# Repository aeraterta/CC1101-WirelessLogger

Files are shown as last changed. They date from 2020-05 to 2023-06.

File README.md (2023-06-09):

# Wireless Data Logging Platform for Human Temperature and Pulse Rate with Networked Mobile Nodes

<p align="center">
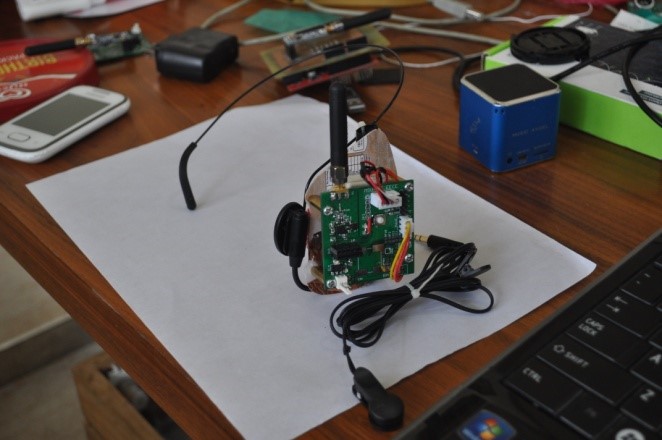
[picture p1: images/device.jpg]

<p>

This is an undergraduate thesis made by Anthony E. Raterta as a requirement for the Degree Bachelor of Science in Electronics and Communications Engineering. 

## Objectives

Generally, the main objective of this study is to construct a prototype of a wireless multi-node data logger that has mobile sensor nodes using transceivers that communicate in the ISM band.

The following are the specific objectives of this study:

1.	To construct a wearable data logger platform.
2.	To utilize the CC1101 transceiver chips for communication.
3.	To attach a temperature and pulse rate sensor in the data logger platform for monitoring human body temperature and pulse rate. 
4.	To identify a suitable location for human body temperature and pulse rate monitoring.

## Methods 

### Flow

The operation of the system imposed is shown in the image below. It contains simplified illustration of the two major parts, the mobile sensor node which may be of any number but for the study, the researcher only made two nodes. The other major part of the system is the receiver node which receives the packets sent by both sensor nodes and dummy nodes.

<p align="center">
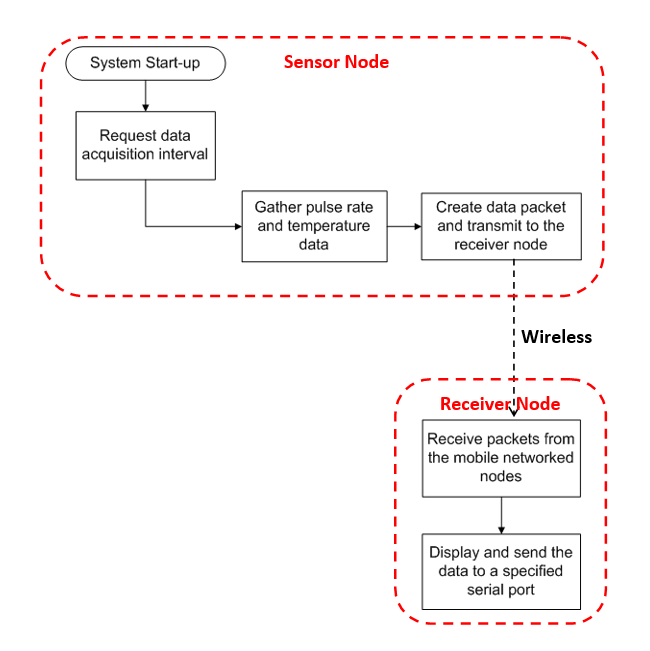
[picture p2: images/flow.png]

<p>

### Block Diagram

Shown in the image below is the physical architecture of the system designed to gather temperature and pulse rate of a patient at an interval set. A single sensor node is composed of an MLX90614 infrared thermometer and an infrared based Grove ear-clip pulse rate sensor.  These modules serve as input devices to an ATmega328p microcontroller unit with a CC1101 RF transceiver working at 433 mega hertz frequency band connected into it and to have the data gathered transmitted into the receiver node which is composed of a CC1101 RF transceiver, an Arduino UNO and a personal computer or a laptop. The microcontroller unit serves as a bridge to have the gathered data stored into the PC or the database pool.

<p align="center">
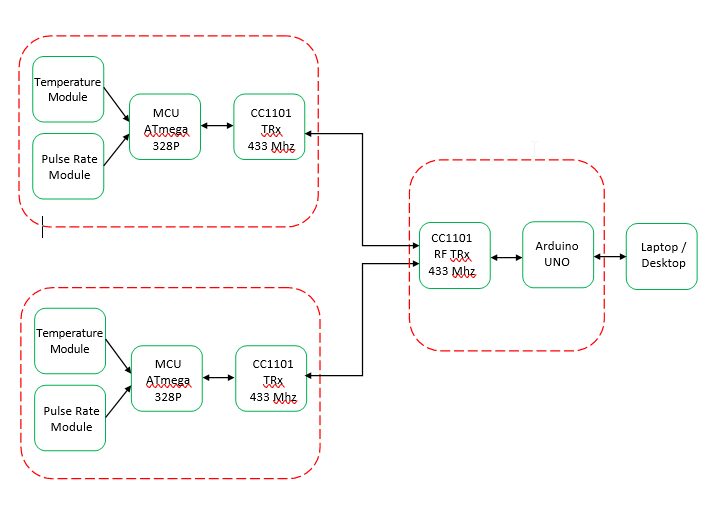
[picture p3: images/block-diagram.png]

<p>

### Materials:

1. MCU - For the device, a programmable ATmega328p microcontroller will be used to do the tasks set. The circuit of an Arduino UNO will be used since its circuit is free and its programming IDE is open source. Also, several supports and forums are available online which would be a great help for the study and could minimize the period of the over-all development process. However, some parts of the Arduino UNO are not usable for the hardware design and may be deemed unnecessary so these parts will be disregarded. Also, the ATmega328p working at 3.3 volts  in the Arduino UNO can also be set to use its internal 8 MHz clock which could be a great option in the aim of minimizing the size of the output device.

2. [MLX90614 Infrared Thermometer](https://www.melexis.com/en/documents/documentation/datasheets/datasheet-mlx90614) - A non-contact MLX90614 Infrared Thermometer working at voltage range of 2.4 – 3.6 volts will be used for the sensor node to gather temperature in degrees Celsius (°C). MLX90614 is best in medical usage with an accuracy of 0.5 degrees Celsius (°C).

3. [Grove Ear-Clip Heart Pulse Sensor](https://wiki.seeedstudio.com/Grove-Ear-clip_Heart_Rate_Sensor/) - The Grove ear-clip pulse sensor is an infrared based sensor that could detect the changes in the density of blood due to the occurrence of pulse during blood circulations. By determining the time interval of the changes of the blood density in the ear lobe, the sensor can have an accurate value of pulse rate.

4. [CC1101 RF Transceiver](http://www.ti.com/lit/ds/symlink/cc1101.pdf?ts=1590260097931) - To maximize the mobility of the sensor node, the transmission of the data gathered from the sensors can be sent wirelessly depending on the choice of media. The effective transmission range for such media should also be maximized so that a bigger scope of a network will be made without jeopardizing the aim of minimizing the power consumption of each component used in the device. To cater such considerations, a CC1101 RF transceiver operating at 433 MHz was used. The said transceiver is capable of naming each node with a specific unique address which is beneficial for the study. A CC1101 RF transceiver break-out module will be used in the early development of the device for testing and debugging purposes. 

5. [Power Supply](https://github.com/aeraterta/CC1101-WirelessLogger/tree/master/Design/ADI-sepic-boost-converter) - The devices uses the ADP1621 SEPIC Converter which supplies a constant 3.3 volts output despite the diminishing value of input voltage ranging from 5 – 3 volts. Such circuit is ideal for mobile data loggers because of its capability of regulating and boosting input voltages.

6. Power Source - Since the main power supply needed for the device needs input voltage ranging from 3 to 5 volts, a mobile phone battery is a good option for such application. 

## Device

### PCB Layout Plan

<p align="center">
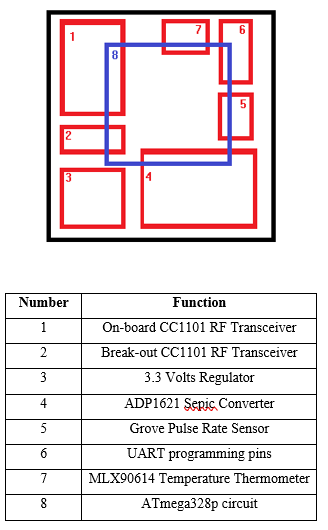
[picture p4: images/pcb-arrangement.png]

<p>

### PCB Layout vs Actual

###### Mobile Node

<p align="center">
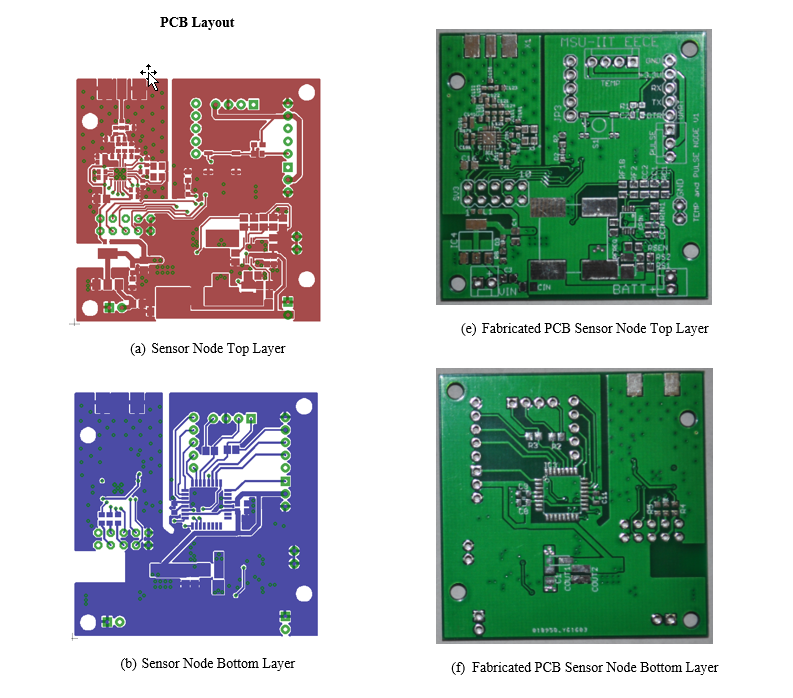
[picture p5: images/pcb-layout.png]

<p>

###### Receiver Node

<p align="center">
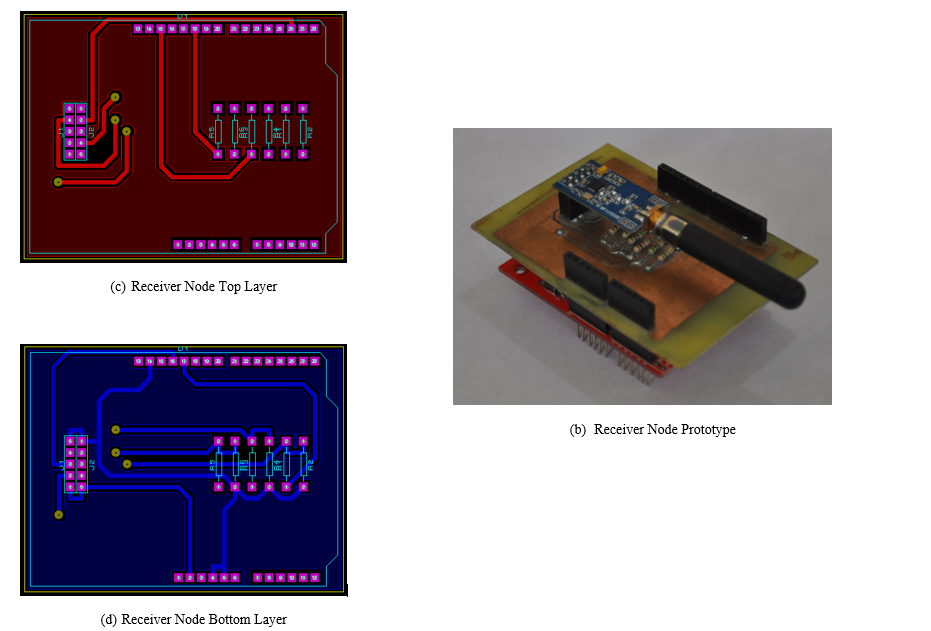
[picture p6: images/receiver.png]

<p>

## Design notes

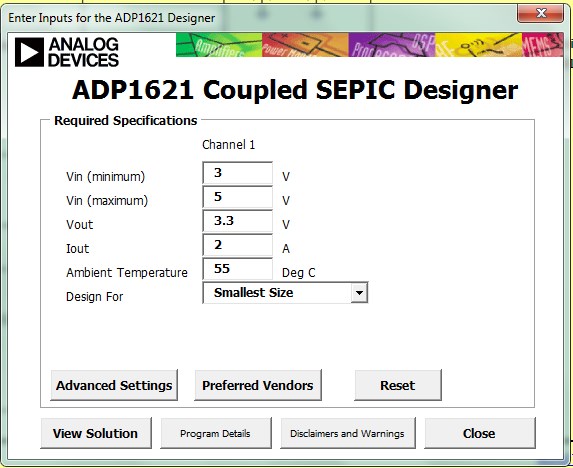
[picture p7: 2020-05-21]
Design/ADI-sepic-boost-converter/specs.jpg

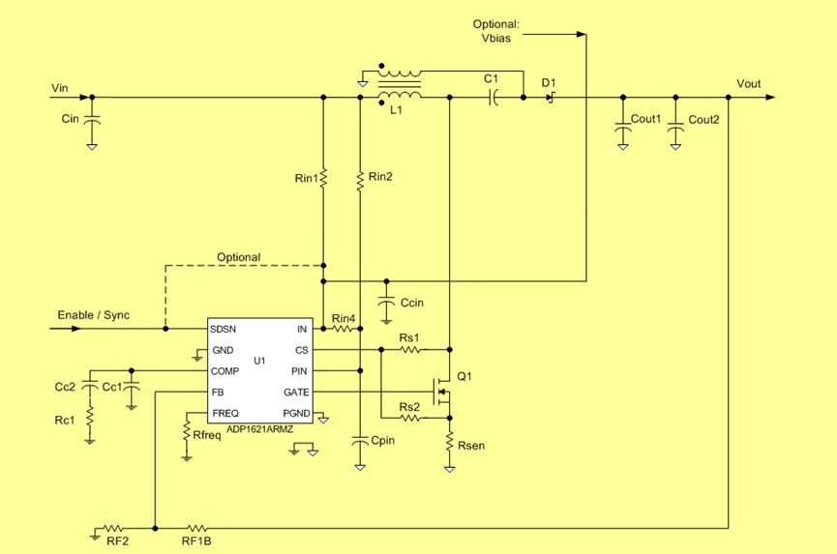
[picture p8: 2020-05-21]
Design/ADI-sepic-boost-converter/ckt.jpg

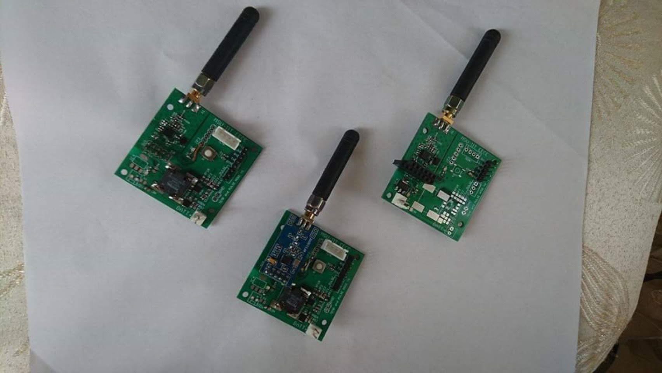
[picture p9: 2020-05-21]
Documentation/Fab-nodes.jpg

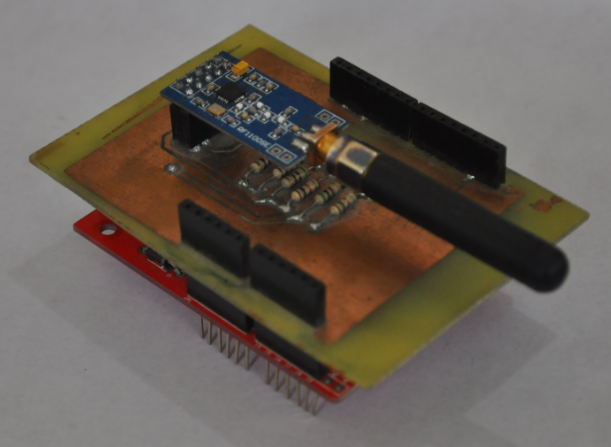
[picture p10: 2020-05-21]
Documentation/Dummy-nodes.png

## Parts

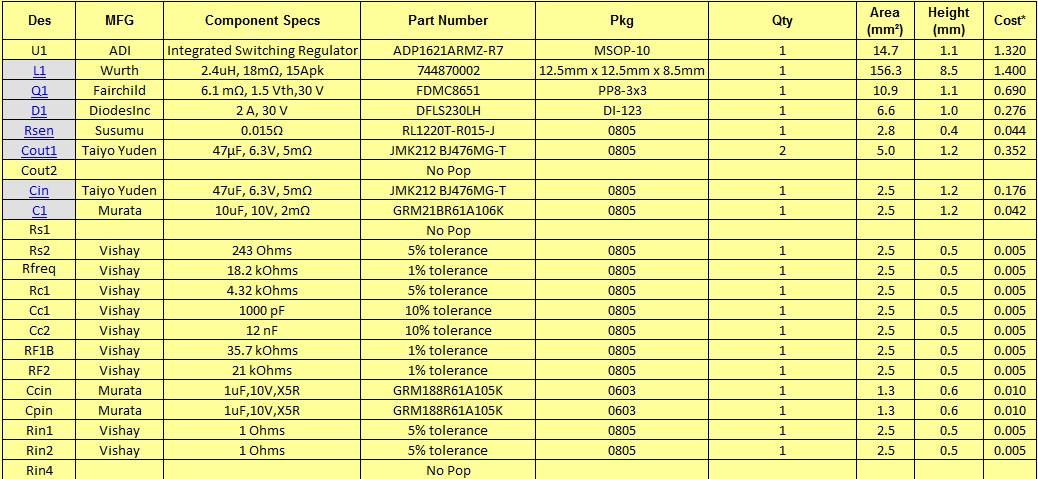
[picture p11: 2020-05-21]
Design/ADI-sepic-boost-converter/materials.jpg

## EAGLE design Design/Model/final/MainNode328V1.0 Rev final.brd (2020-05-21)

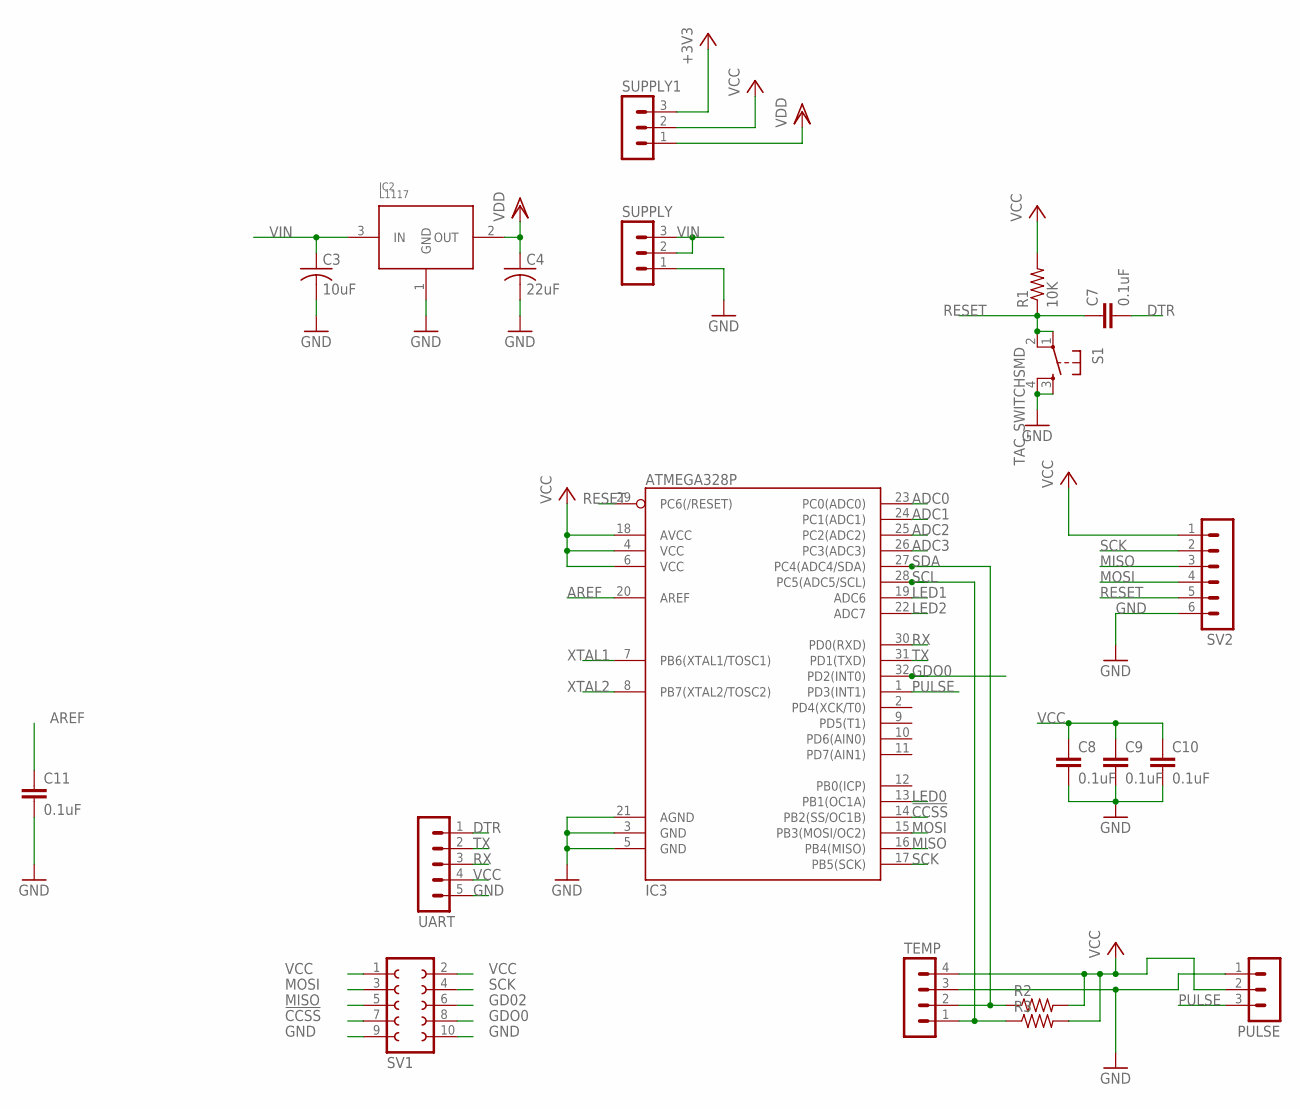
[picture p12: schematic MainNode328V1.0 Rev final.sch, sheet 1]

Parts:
C3: 10uF; C0805; MPN 06034D106MAT2A
C4: 22uF; C0805; MPN 06034D106MAT2A
C7, C8, C9, C10, C11: 0.1uF; 0805
IC2: L1117; DPACK
IC3: ATMEGA328P; TQFP32-08
PULSE: MA03-1
R1: 10K; 0603-RES
R2, R3: R-US_R0805; R0805
S1: TAC_SWITCHSMD; TACTILE-SWITCH-SMD
SUPPLY, SUPPLY1: MA03-1
SV1: FE05-2
SV2: MA06-1
TEMP: MA04-1
UART: MA05-1

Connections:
!CCSS: IC3.14 (PB2(SS/OC1B)), SV1.7
+3V3: SUPPLY1.3; also elsewhere on the board
ADC0: IC3.23 (PC0(ADC0))
ADC1: IC3.24 (PC1(ADC1))
ADC2: IC3.25 (PC2(ADC2))
ADC3: IC3.26 (PC3(ADC3))
AREF: C11.1, IC3.20 (AREF)
DTR: C7.2, UART.1
GD02: SV1.6
GDO0: IC3.32 (PD2(INT0)), SV1.8
GND: C3.2, C4.2, C8.2, C9.2, C10.2, C11.2, IC2.1 (GND), IC3.3 (GND), IC3.5 (GND), IC3.21 (AGND), PULSE.1, S1.3, S1.4, SUPPLY.1, SV1.9, SV1.10, SV2.6, TEMP.3, UART.5; also elsewhere on the board
LED0: IC3.13 (PB1(OC1A))
LED1: IC3.19 (ADC6)
LED2: IC3.22 (ADC7)
MISO: IC3.16 (PB4(MISO)), SV1.5, SV2.3
MOSI: IC3.15 (PB3(MOSI/OC2)), SV1.3, SV2.4
PULSE: IC3.1 (PD3(INT1)), PULSE.3
RESET: C7.1, IC3.29 (PC6(/RESET)), R1.1, S1.1, S1.2, SV2.5
RX: IC3.30 (PD0(RXD)), UART.3
SCK: IC3.17 (PB5(SCK)), SV1.4, SV2.2
SCL: IC3.28 (PC5(ADC5/SCL)), R3.1, TEMP.1
SDA: IC3.27 (PC4(ADC4/SDA)), R2.1, TEMP.2
TX: IC3.31 (PD1(TXD)), UART.2
VCC: C8.1, C9.1, C10.1, IC3.4 (VCC), IC3.6 (VCC), IC3.18 (AVCC), PULSE.2, R1.2, R2.2, R3.2, SUPPLY1.2, SV1.1, SV1.2, SV2.1, TEMP.4, UART.4
VDD: C4.1, IC2.2 (OUT), SUPPLY1.1
VIN: C3.1, IC2.3 (IN), SUPPLY.2, SUPPLY.3
XTAL1: IC3.7 (PB6(XTAL1/TOSC1))
XTAL2: IC3.8 (PB7(XTAL2/TOSC2))

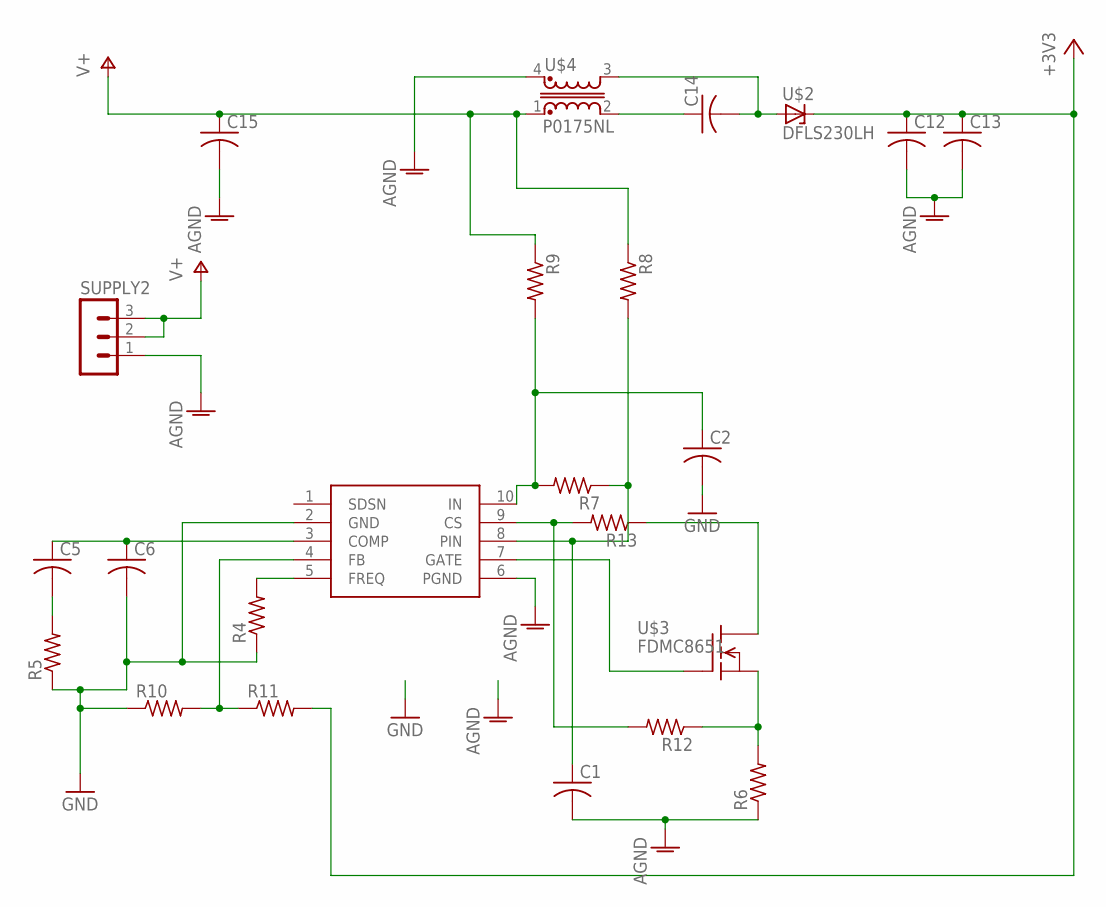
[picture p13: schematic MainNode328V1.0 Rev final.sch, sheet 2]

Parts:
C1, C2: C-USC0603K; C0603K
C5, C6, C12, C13, C14, C15: C-USC0805K; C0805K
R4, R5, R6, R7, R8, R9, R10, R11, R12, R13: R-US_R0805; R0805
SUPPLY2: MA03-1
U$1: ADP1621; MSOP10
U$2: DFLS230LH; DI123
U$3: FDMC8651; PP8-3X3
U$4: P0175NL; INDUCTOR

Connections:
+3V3: C12.1, C13.1, R11.2, U$2.C; also elsewhere on the board
AGND: C1.2, C12.2, C13.2, C15.2, R6.1, SUPPLY2.1, U$1.6 (PGND), U$4.4 (1)
GND: C2.2, C6.2, R4.1, R5.1, R10.1, U$1.2 (GND); also elsewhere on the board
unnamed: R4.2, U$1.5 (FREQ)
unnamed: C2.1, R7.2, R9.2, U$1.10 (IN)
unnamed: C1.1, R7.1, R8.2, U$1.8 (PIN)
unnamed: R10.2, R11.1, U$1.4 (FB)
unnamed: R6.2, R12.1, U$3.1 (S), U$3.2 (S), U$3.3 (S)
unnamed: R12.2, R13.2, U$1.9 (CS)
unnamed: U$1.7 (GATE), U$3.4 (G)
unnamed: R13.1, U$3.5 (D), U$3.6 (D), U$3.7 (D), U$3.8 (D), U$3.9 (D)
unnamed: C5.1, C6.1, U$1.3 (COMP)
unnamed: C5.2, R5.2
unnamed: C14.1, U$4.2 (4)
unnamed: C14.2, U$2.A, U$4.3 (2)
V+: C15.1, R8.1, R9.1, SUPPLY2.2, SUPPLY2.3, U$4.1 (3)

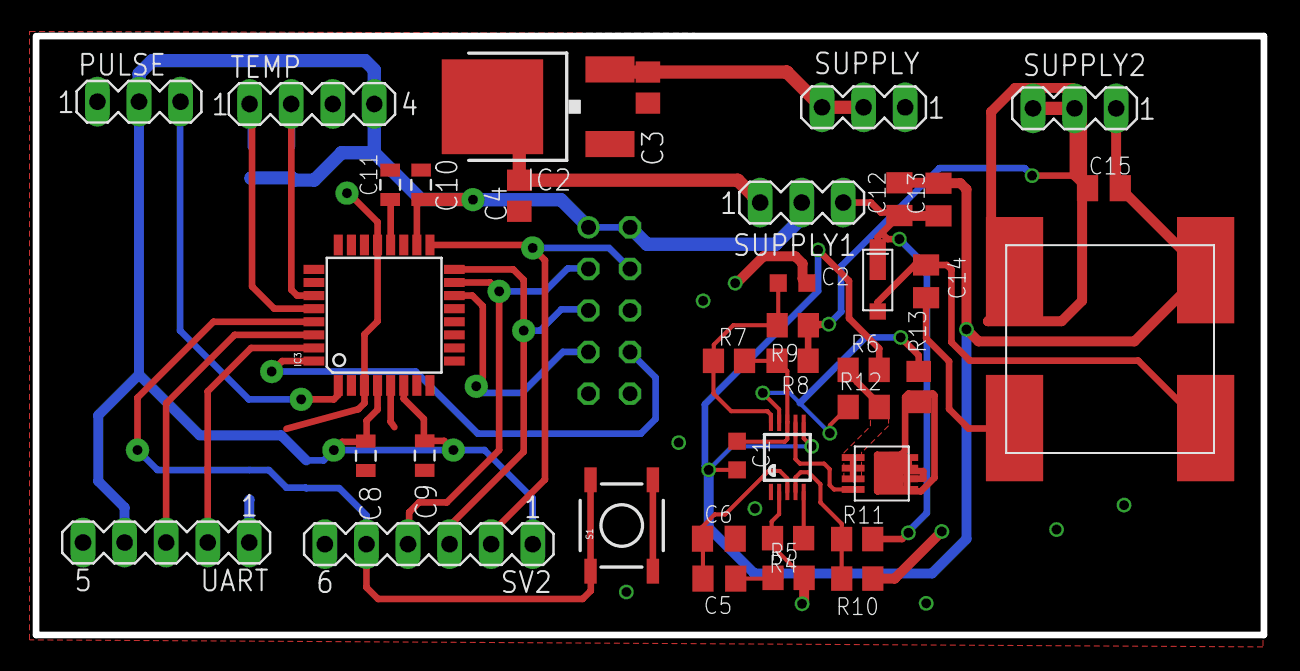
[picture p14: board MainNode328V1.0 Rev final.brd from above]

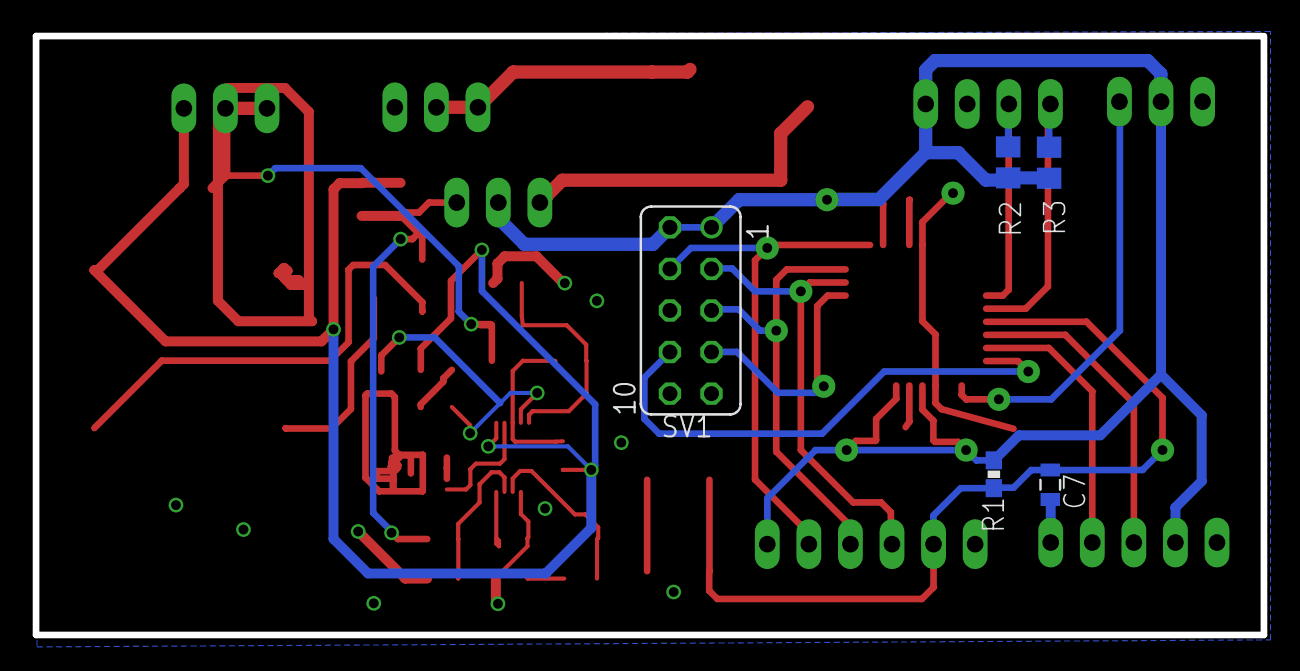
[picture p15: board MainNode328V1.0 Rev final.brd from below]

Board: 2 copper layers, 75.0 x 36.6 mm, 43 parts (5 on the bottom side), 32 nets.

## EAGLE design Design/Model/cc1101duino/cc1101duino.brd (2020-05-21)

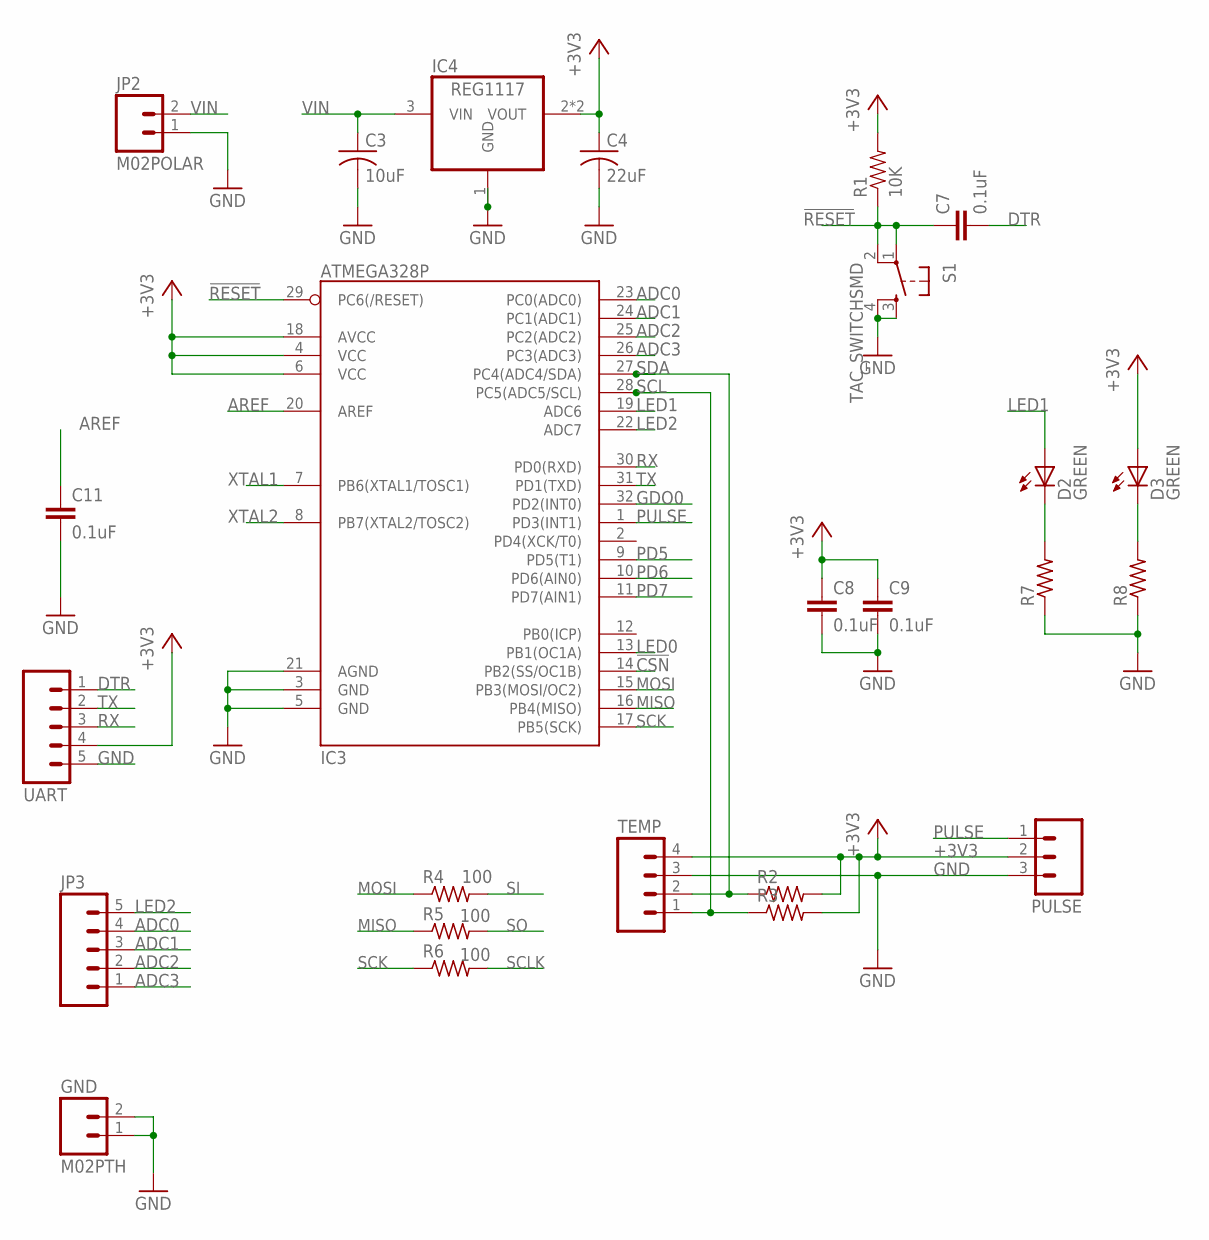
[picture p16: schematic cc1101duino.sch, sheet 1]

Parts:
C3: 10uF; C0805; MPN 06034D106MAT2A
C4: 22uF; C0805; MPN 06034D106MAT2A
C7, C8, C9, C11: 0.1uF; 0805
D2, D3: GREEN; LED-0603
GND: M02PTH; 1X02
IC3: ATMEGA328P; TQFP32-08
IC4: REG1117; SOT223
JP2: M02POLAR; MOLEX-1X2
JP3: M05PTH; 1X05
PULSE: M03POLAR; MOLEX-1X3
R1: 10K; 0603-RES
R2, R3: R-US_R0805; R0805
R4, R5, R6: 100; R0603
R7, R8: R-US_R0603; R0603
S1: TAC_SWITCHSMD; TACTILE-SWITCH-SMD
TEMP: M04POLAR; MOLEX-1X4
UART: M05PTH; 1X05

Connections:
!CSN: IC3.14 (PB2(SS/OC1B)); also elsewhere on the board
!RESET: C7.1, IC3.29 (PC6(/RESET)), R1.1, S1.1, S1.2
+3V3: C4.1, C8.1, C9.1, D3.A, IC3.4 (VCC), IC3.6 (VCC), IC3.18 (AVCC), IC4.2 (VOUT), IC4.4 (VOUT), PULSE.2, R1.2, R2.2, R3.2, TEMP.4, UART.4; also elsewhere on the board
ADC0: IC3.23 (PC0(ADC0)), JP3.4
ADC1: IC3.24 (PC1(ADC1)), JP3.3
ADC2: IC3.25 (PC2(ADC2)), JP3.2
ADC3: IC3.26 (PC3(ADC3)), JP3.1
AREF: C11.1, IC3.20 (AREF)
DTR: C7.2, UART.1
GDO0: IC3.32 (PD2(INT0)); also elsewhere on the board
GND: C3.2, C4.2, C8.2, C9.2, C11.2, GND.1, GND.2, IC3.3 (GND), IC3.5 (GND), IC3.21 (AGND), IC4.1 (GND), JP2.1, PULSE.3, R7.1, R8.1, S1.3, S1.4, TEMP.3, UART.5; also elsewhere on the board
LED0: IC3.13 (PB1(OC1A))
LED1: D2.A, IC3.19 (ADC6)
LED2: IC3.22 (ADC7), JP3.5
MISO: IC3.16 (PB4(MISO)), R5.1; also elsewhere on the board
MOSI: IC3.15 (PB3(MOSI/OC2)), R4.1; also elsewhere on the board
unnamed: D2.C, R7.2
unnamed: D3.C, R8.2
PD5: IC3.9 (PD5(T1))
PD6: IC3.10 (PD6(AIN0))
PD7: IC3.11 (PD7(AIN1))
PULSE: IC3.1 (PD3(INT1)), PULSE.1
RX: IC3.30 (PD0(RXD)), UART.3
SCK: IC3.17 (PB5(SCK)), R6.1; also elsewhere on the board
SCL: IC3.28 (PC5(ADC5/SCL)), R3.1, TEMP.1
SCLK: R6.2; also elsewhere on the board
SDA: IC3.27 (PC4(ADC4/SDA)), R2.1, TEMP.2
SI: R4.2; also elsewhere on the board
SO: R5.2; also elsewhere on the board
TX: IC3.31 (PD1(TXD)), UART.2
VIN: C3.1, IC4.3 (VIN), JP2.2
XTAL1: IC3.7 (PB6(XTAL1/TOSC1))
XTAL2: IC3.8 (PB7(XTAL2/TOSC2))

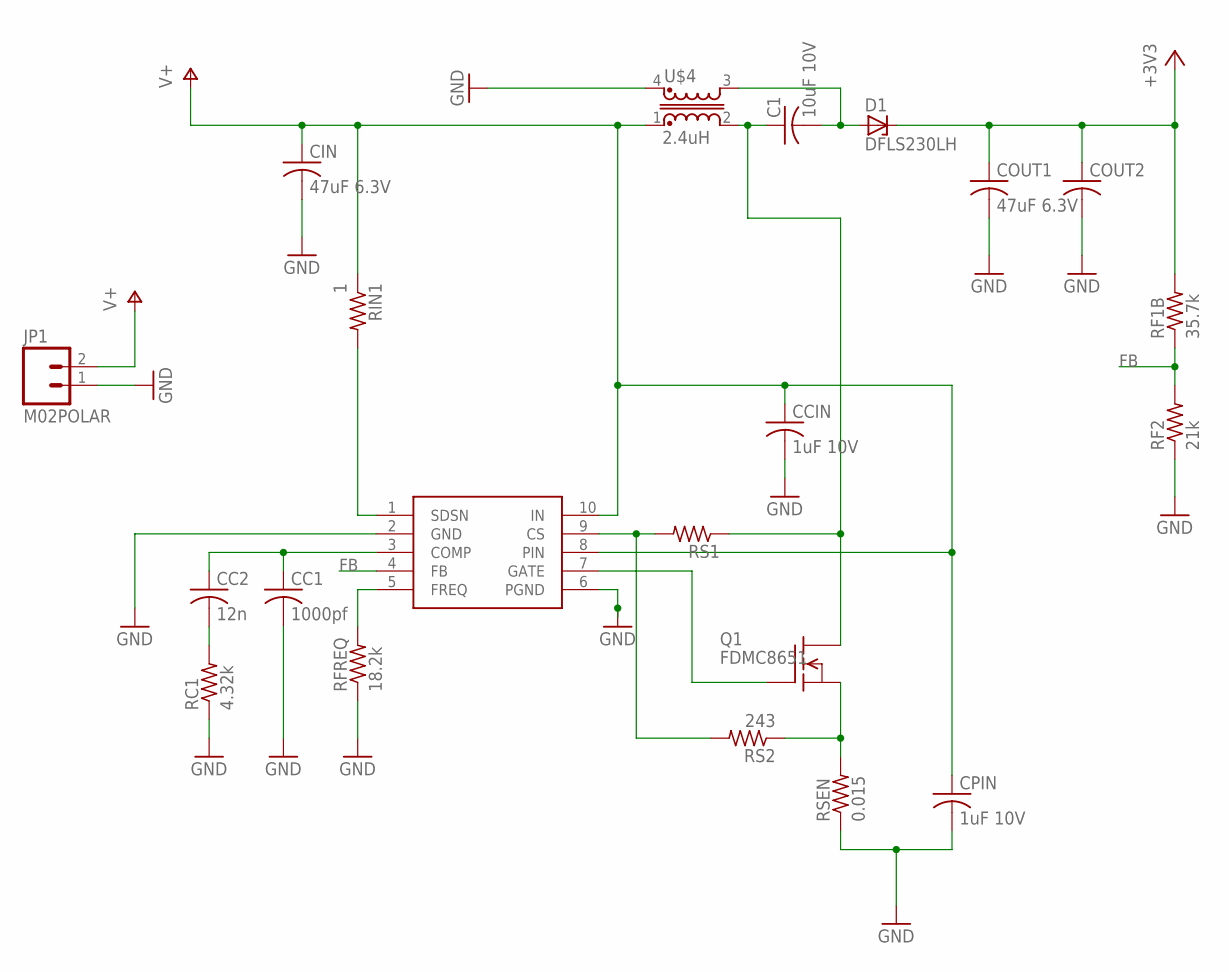
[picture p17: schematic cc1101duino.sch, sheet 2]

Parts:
C1: 10uF 10V; C0805K
CC1: 1000pf; C0805K
CC2: 12n; C0805K
CCIN: 1uF 10V; C0603K
CIN: 47uF 6.3V; C0805K
COUT1: 47uF 6.3V; C0805K
COUT2: C-USC0805K; C0805K
CPIN: 1uF 10V; C0603K
D1: DFLS230LH; DI123
JP1: M02POLAR; MOLEX-1X2
Q1: FDMC8651; PP8-3X3
RC1: 4.32k; R0805
RF1B: 35.7k; R0805
RF2: 21k; R0805
RFREQ: 18.2k; R0805
RIN1: 1; R0805
RS1: R-US_R0805; R0805
RS2: 243; R0805
RSEN: 0.015; R0805
U$1: ADP1621; MSOP10
U$4: 2.4uH; INDUCTOR

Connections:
+3V3: COUT1.1, COUT2.1, D1.C, RF1B.2; also elsewhere on the board
C1: C1.2, D1.A, U$4.3 (2)
FB: RF1B.1, RF2.2, U$1.4 (FB)
GND: CC1.2, CCIN.2, CIN.2, COUT1.2, COUT2.2, CPIN.2, JP1.1, RC1.1, RF2.1, RFREQ.1, RSEN.1, U$1.2 (GND), U$1.6 (PGND), U$4.4 (1); also elsewhere on the board
unnamed: RFREQ.2, U$1.5 (FREQ)
unnamed: RIN1.2, U$1.1 (SDSN)
unnamed: Q1.1 (S), Q1.2 (S), Q1.3 (S), RS2.1, RSEN.2
unnamed: RS1.2, RS2.2, U$1.9 (CS)
unnamed: Q1.4 (G), U$1.7 (GATE)
unnamed: CC1.1, CC2.1, U$1.3 (COMP)
unnamed: CC2.2, RC1.2
unnamed: C1.1, Q1.5 (D), Q1.6 (D), Q1.7 (D), Q1.8 (D), Q1.9 (D), RS1.1, U$4.2 (4)
V+: CCIN.1, CIN.1, CPIN.1, JP1.2, RIN1.1, U$1.8 (PIN), U$1.10 (IN), U$4.1 (3)

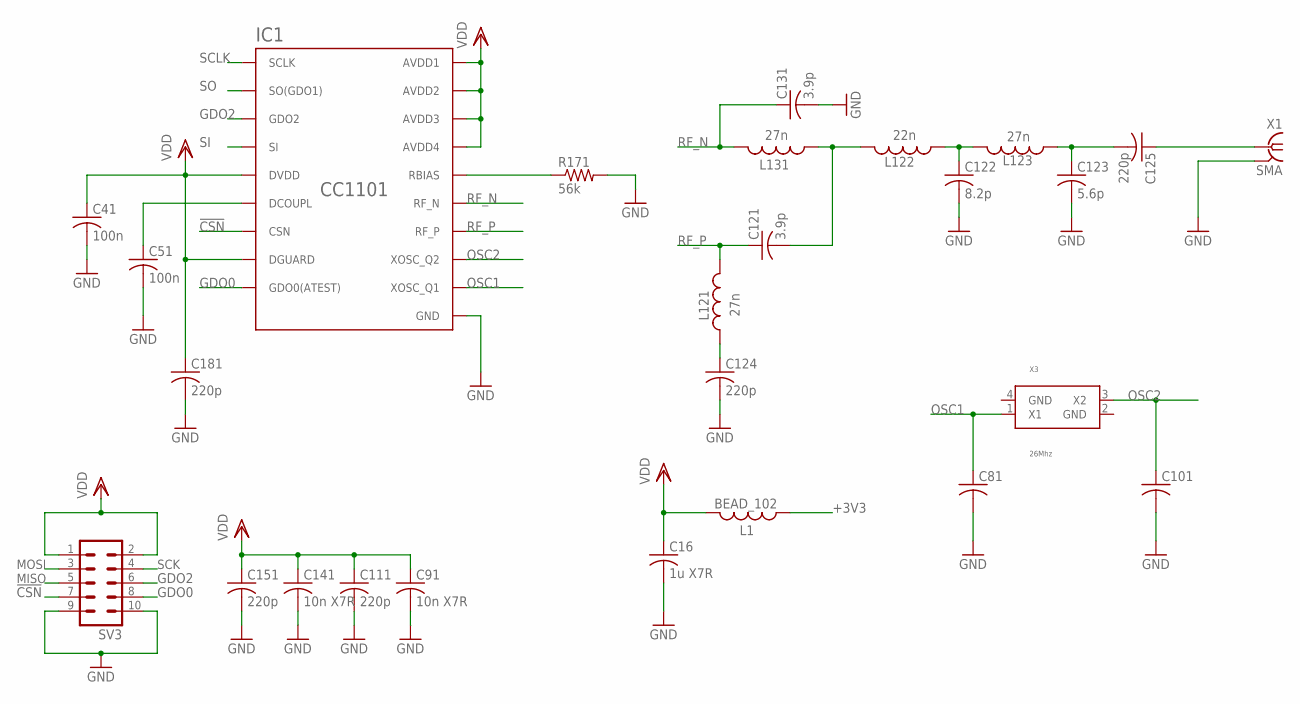
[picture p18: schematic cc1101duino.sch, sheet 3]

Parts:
C16: 1u X7R; C0805
C41, C51: 100n; C0402
C81, C101: C-USC0402; C0402
C91, C141: 10n X7R; C0402
C111, C124, C125, C151, C181: 220p; C0402
C121, C131: 3.9p; C0402
C122: 8.2p; C0402
C123: 5.6p; C0402
IC1: CC1101; QLP20
L1: BEAD_102; C0402
L121, L123, L131: 27n; C0402
L122: 22n; C0402
R171: 56k; R0402
SV3: MA05-2
X1: SMA; J502-ND-142-0711-821/826
X3: 26Mhz; ABM8G

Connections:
!CSN: IC1.7 (CSN), SV3.7; also elsewhere on the board
+3V3: L1.1; also elsewhere on the board
GDO0: IC1.6 (GDO0(ATEST)), SV3.8; also elsewhere on the board
GDO2: IC1.3 (GDO2), SV3.6
GND: C16.2, C41.2, C51.2, C81.2, C91.2, C101.2, C111.2, C122.2, C123.2, C124.2, C131.2, C141.2, C151.2, C181.2, IC1.16 (GND), IC1.19 (GND), IC1.GND, IC1.GND1 (GND), IC1.GND2 (GND), IC1.GND3 (GND), IC1.GND4 (GND), IC1.GND5 (GND), R171.2, SV3.9, SV3.10, X1.G@1 (2), X1.G@2 (2), X1.G@3 (2), X1.G@4 (2); also elsewhere on the board
MISO: SV3.5; also elsewhere on the board
MOSI: SV3.3; also elsewhere on the board
unnamed: C125.1, X1.1
unnamed: IC1.17 (RBIAS), R171.1
unnamed: C51.1, IC1.5 (DCOUPL)
unnamed: C121.2, L122.2, L131.1
unnamed: C124.1, L121.1
unnamed: C122.1, L122.1, L123.2
unnamed: C123.1, C125.2, L123.1
OSC1: C81.1, IC1.8 (XOSC_Q1), X3.1 (X1)
OSC2: C101.1, IC1.10 (XOSC_Q2), X3.3 (X2)
RF_N: C131.1, IC1.13 (RF_N), L131.2
RF_P: C121.1, IC1.12 (RF_P), L121.2
SCK: SV3.4; also elsewhere on the board
SCLK: IC1.1 (SCLK); also elsewhere on the board
SI: IC1.20 (SI); also elsewhere on the board
SO: IC1.2 (SO(GDO1)); also elsewhere on the board
VDD: C16.1, C41.1, C91.1, C111.1, C141.1, C151.1, C181.1, IC1.4 (DVDD), IC1.9 (AVDD1), IC1.11 (AVDD2), IC1.14 (AVDD3), IC1.15 (AVDD4), IC1.18 (DGUARD), L1.2, SV3.1, SV3.2

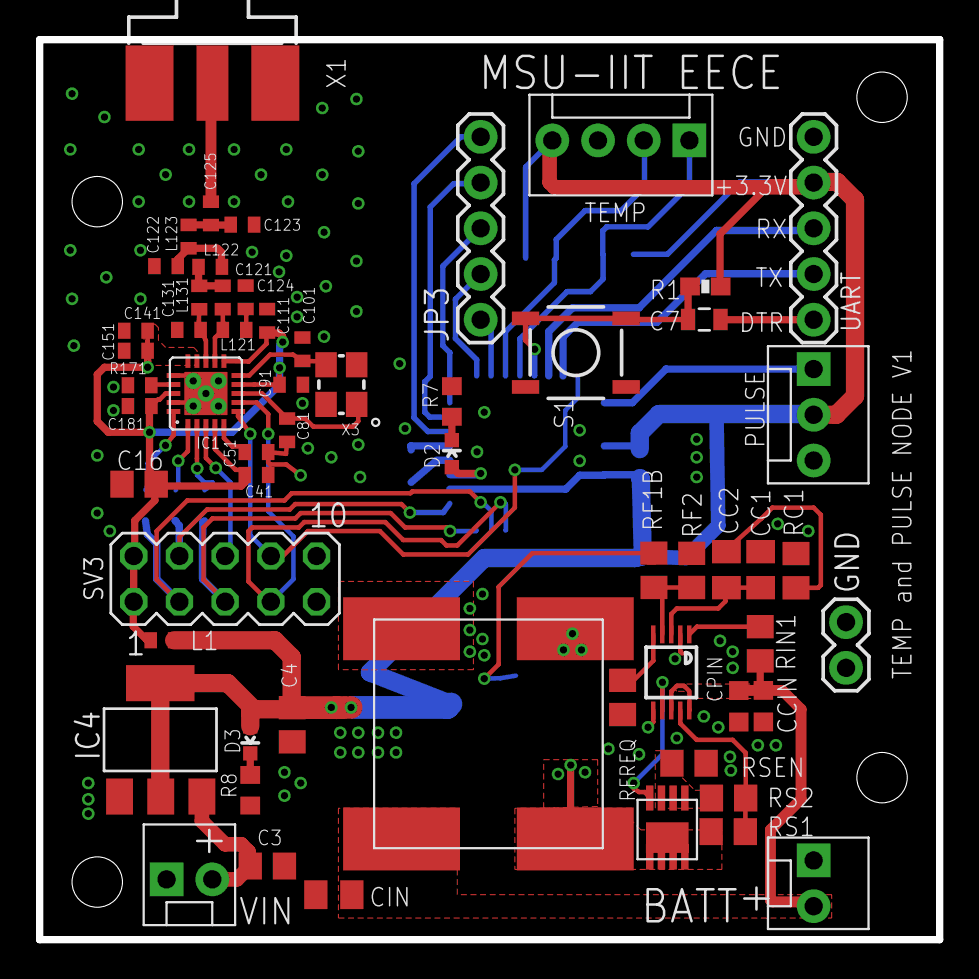
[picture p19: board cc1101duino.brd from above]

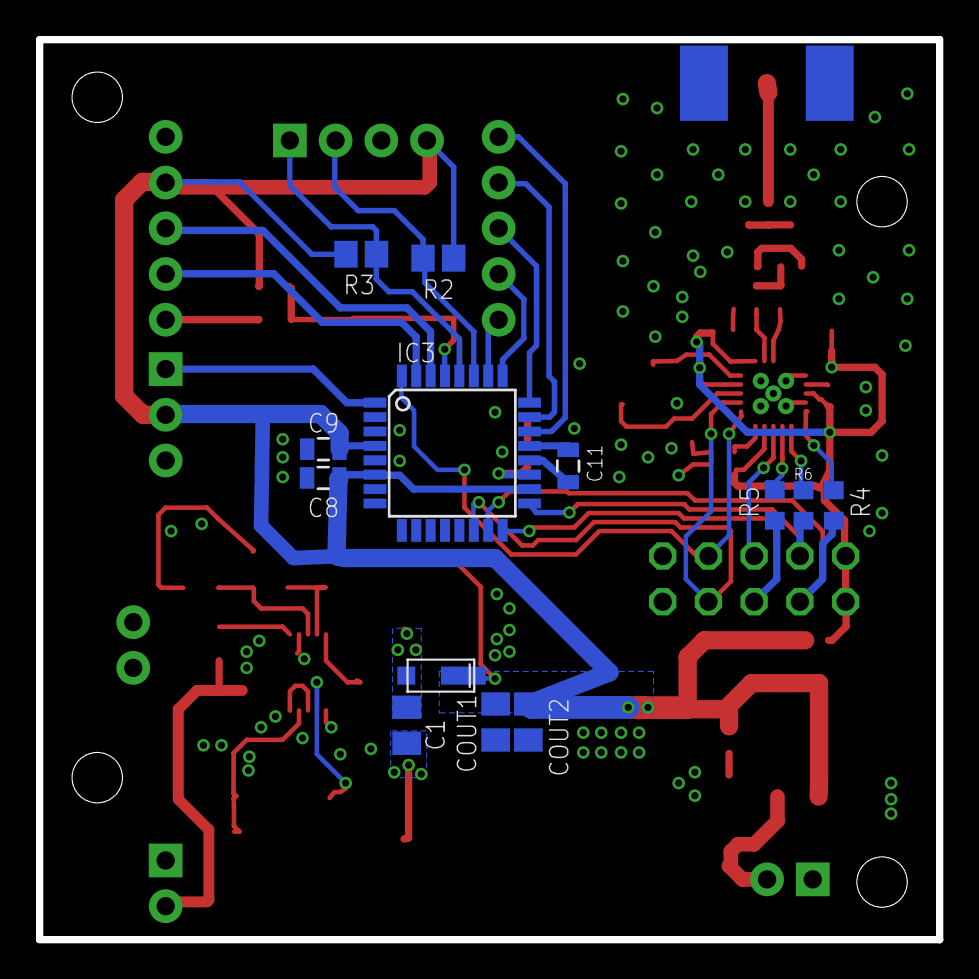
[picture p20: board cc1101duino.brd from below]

Board: 2 copper layers, 50.0 x 50.0 mm, 72 parts (13 on the bottom side), 51 nets.

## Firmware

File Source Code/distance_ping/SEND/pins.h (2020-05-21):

#ifndef _PINS_H
#define _PINS_H

#include "Arduino.h"

/**
 * SPI pins -- Modified for GIZDUINO-X
 */

//#define MEGA



#define LED0	9	
#define LED1	A6	
#define LED2	A7	


#ifdef MEGA

#define SPI_SS   10     // PB0 = SPI_SS Pin_10
#define SPI_MOSI 11     // PB2 = MOSI Pin_11
#define SPI_MISO 12     // PB3 = MISO
#define SPI_SCK  13     // PB1 = SCK
#define GDO0     2     // PE4= INT0

#define PORT_SPI_MISO  PINB
#define BIT_SPI_MISO  3

#define PORT_SPI_SS  PORTB
#define BIT_SPI_SS   0

#define PORT_GDO0  PINE
#define BIT_GDO0 4

  //ADE SS pin
#define ADE_SS 5

//soft SPI
#define _MISO  8
#define _MOSI  6
#define _SCK   7
#define _SS  ADE_SS




 //ADE IRQ pin
#define ADE_IRQ 3

#else

#define SPI_SS   10     // PB2 = SPI_SS Pin_10
#define SPI_MOSI 11     // PB3 = MOSI Pin_11
#define SPI_MISO 12     // PB4 = MISO
#define SPI_SCK  13     // PB5 = SCK
#define GDO0     2     // PD2 = INT0

#define PORT_SPI_MISO  PINB
#define BIT_SPI_MISO  4

#define PORT_SPI_SS  PORTB
#define BIT_SPI_SS   2

#define PORT_GDO0  PIND
#define BIT_GDO0 2

//ADE SS pin
#define ADE_SS 5   //PB1 = ADESS

//soft SPI
//soft SPI
#define _MISO  8
#define _MOSI  6
#define _SCK   7
#define _SS  ADE_SS

 

 //ADE IRQ pin
#define ADE_IRQ 3   //PD3 = INT1

#endif


#endif

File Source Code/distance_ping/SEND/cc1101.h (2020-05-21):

/**
 * Copyright (c) 2011 panStamp <contact@panstamp.com>
 * 
 * This file is part of the panStamp project.
 * 
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
 * Author: Daniel Berenguer
 * Creation date: 03/03/2011
 */

#ifndef _CC1101_H
#define _CC1101_H

#include "Arduino.h"
#include "spiz.h"
#include "pins.h"
#include "ccpacket.h"

/**
 * Carrier frequencies
 */
enum CFREQ
{
  CFREQ_868 = 0,
  CFREQ_915,
  CFREQ_433,
  CFREQ_LAST
};

/**
 * RF STATES
 */
enum RFSTATE
{
  RFSTATE_IDLE = 0,
  RFSTATE_RX,
  RFSTATE_TX
};


/**
 * Frequency channels
 */
#define NUMBER_OF_FCHANNELS      10

/**
 * Type of transfers
 */
#define WRITE_BURST              0x40
#define READ_SINGLE              0x80
#define READ_BURST               0xC0

/**
 * Type of register
 */
#define CC1101_CONFIG_REGISTER   READ_SINGLE
#define CC1101_STATUS_REGISTER   READ_BURST

/**
 * PATABLE & FIFO's
 */
#define CC1101_PATABLE           0x3E        // PATABLE address
#define CC1101_TXFIFO            0x3F        // TX FIFO address
#define CC1101_RXFIFO            0x3F        // RX FIFO address

/**
 * Command strobes
 */
#define CC1101_SRES              0x30        // Reset CC1101 chip
#define CC1101_SFSTXON           0x31        // Enable and calibrate frequency synthesizer (if MCSM0.FS_AUTOCAL=1). If in RX (with CCA):
                                             // Go to a wait state where only the synthesizer is running (for quick RX / TX turnaround).
#define CC1101_SXOFF             0x32        // Turn off crystal oscillator
#define CC1101_SCAL              0x33        // Calibrate frequency synthesizer and turn it off. SCAL can be strobed from IDLE mode without
                                             // setting manual calibration mode (MCSM0.FS_AUTOCAL=0)
#define CC1101_SRX               0x34        // Enable RX. Perform calibration first if coming from IDLE and MCSM0.FS_AUTOCAL=1
#define CC1101_STX               0x35        // In IDLE state: Enable TX. Perform calibration first if MCSM0.FS_AUTOCAL=1.
                                             // If in RX state and CCA is enabled: Only go to TX if channel is clear
#define CC1101_SIDLE             0x36        // Exit RX / TX, turn off frequency synthesizer and exit Wake-On-Radio mode if applicable
#define CC1101_SWOR              0x38        // Start automatic RX polling sequence (Wake-on-Radio) as described in Section 19.5 if
                                             // WORCTRL.RC_PD=0
#define CC1101_SPWD              0x39        // Enter power down mode when CSn goes high
#define CC1101_SFRX              0x3A        // Flush the RX FIFO buffer. Only issue SFRX in IDLE or RXFIFO_OVERFLOW states
#define CC1101_SFTX              0x3B        // Flush the TX FIFO buffer. Only issue SFTX in IDLE or TXFIFO_UNDERFLOW states
#define CC1101_SWORRST           0x3C        // Reset real time clock to Event1 value
#define CC1101_SNOP              0x3D        // No operation. May be used to get access to the chip status byte

/**
 * CC1101 configuration registers
 */
#define CC1101_IOCFG2            0x00        // GDO2 Output Pin Configuration
#define CC1101_IOCFG1            0x01        // GDO1 Output Pin Configuration
#define CC1101_IOCFG0            0x02        // GDO0 Output Pin Configuration
#define CC1101_FIFOTHR           0x03        // RX FIFO and TX FIFO Thresholds
#define CC1101_SYNC1             0x04        // Sync Word, High Byte
#define CC1101_SYNC0             0x05        // Sync Word, Low Byte
#define CC1101_PKTLEN            0x06        // Packet Length
#define CC1101_PKTCTRL1          0x07        // Packet Automation Control
#define CC1101_PKTCTRL0          0x08        // Packet Automation Control
#define CC1101_ADDR              0x09        // Device Address
#define CC1101_CHANNR            0x0A        // Channel Number
#define CC1101_FSCTRL1           0x0B        // Frequency Synthesizer Control
#define CC1101_FSCTRL0           0x0C        // Frequency Synthesizer Control
#define CC1101_FREQ2             0x0D        // Frequency Control Word, High Byte
#define CC1101_FREQ1             0x0E        // Frequency Control Word, Middle Byte
#define CC1101_FREQ0             0x0F        // Frequency Control Word, Low Byte
#define CC1101_MDMCFG4           0x10        // Modem Configuration
#define CC1101_MDMCFG3           0x11        // Modem Configuration
#define CC1101_MDMCFG2           0x12        // Modem Configuration
#define CC1101_MDMCFG1           0x13        // Modem Configuration
#define CC1101_MDMCFG0           0x14        // Modem Configuration
#define CC1101_DEVIATN           0x15        // Modem Deviation Setting
#define CC1101_MCSM2             0x16        // Main Radio Control State Machine Configuration
#define CC1101_MCSM1             0x17        // Main Radio Control State Machine Configuration
#define CC1101_MCSM0             0x18        // Main Radio Control State Machine Configuration
#define CC1101_FOCCFG            0x19        // Frequency Offset Compensation Configuration
#define CC1101_BSCFG             0x1A        // Bit Synchronization Configuration
#define CC1101_AGCCTRL2          0x1B        // AGC Control
#define CC1101_AGCCTRL1          0x1C        // AGC Control
#define CC1101_AGCCTRL0          0x1D        // AGC Control
#define CC1101_WOREVT1           0x1E        // High Byte Event0 Timeout
#define CC1101_WOREVT0           0x1F        // Low Byte Event0 Timeout
#define CC1101_WORCTRL           0x20        // Wake On Radio Control
#define CC1101_FREND1            0x21        // Front End RX Configuration
#define CC1101_FREND0            0x22        // Front End TX Configuration
#define CC1101_FSCAL3            0x23        // Frequency Synthesizer Calibration
#define CC1101_FSCAL2            0x24        // Frequency Synthesizer Calibration
#define CC1101_FSCAL1            0x25        // Frequency Synthesizer Calibration
#define CC1101_FSCAL0            0x26        // Frequency Synthesizer Calibration
#define CC1101_RCCTRL1           0x27        // RC Oscillator Configuration
#define CC1101_RCCTRL0           0x28        // RC Oscillator Configuration
#define CC1101_FSTEST            0x29        // Frequency Synthesizer Calibration Control
#define CC1101_PTEST             0x2A        // Production Test
#define CC1101_AGCTEST           0x2B        // AGC Test
#define CC1101_TEST2             0x2C        // Various Test Settings
#define CC1101_TEST1             0x2D        // Various Test Settings
#define CC1101_TEST0             0x2E        // Various Test Settings

/**
 * Status registers
 */
#define CC1101_PARTNUM           0x30        // Chip ID
#define CC1101_VERSION           0x31        // Chip ID
#define CC1101_FREQEST           0x32        // Frequency Offset Estimate from Demodulator
#define CC1101_LQI               0x33        // Demodulator Estimate for Link Quality
#define CC1101_RSSI              0x34        // Received Signal Strength Indication
#define CC1101_MARCSTATE         0x35        // Main Radio Control State Machine State
#define CC1101_WORTIME1          0x36        // High Byte of WOR Time
#define CC1101_WORTIME0          0x37        // Low Byte of WOR Time
#define CC1101_PKTSTATUS         0x38        // Current GDOx Status and Packet Status
#define CC1101_VCO_VC_DAC        0x39        // Current Setting from PLL Calibration Module
#define CC1101_TXBYTES           0x3A        // Underflow and Number of Bytes
#define CC1101_RXBYTES           0x3B        // Overflow and Number of Bytes
#define CC1101_RCCTRL1_STATUS    0x3C        // Last RC Oscillator Calibration Result
#define CC1101_RCCTRL0_STATUS    0x3D        // Last RC Oscillator Calibration Result 


/**
 * CC1101 configuration registers - Default values extracted from SmartRF Studio
 *
 * Configuration:
 *
 * Deviation = 5.157471 
 * Base frequency = 433.999969 
 * Carrier frequency = 433.999969
 * Channel number = 0 
 * Carrier frequency = 433.999969
 * Modulated = true 
 * Modulation format = GFSK 
 * Manchester enable = false
 * Data whitening = off
 * Sync word qualifier mode = 30/32 sync word bits detected 
 * Preamble count = 4 
 * Channel spacing = 199.951172
 * Carrier frequency = 433.999969
 * Data rate = 2.39897
 * RX filter BW = 58.035714
 * Data format = Normal mode 
 * Length config = Variable packet length mode. Packet length configured by the first byte after sync word 
 * CRC enable = true 
 * Packet length = 255 
 * Device address = 1 
 * Address config = Enable address check
 * Append status = Append two status bytes to the payload of the packet. The status bytes contain RSSI and
 * LQI values, as well as CRC OK
 * CRC autoflush = false 
 * PA ramping = false 
 * TX power = 0
 * GDO0 mode = Asserts when sync word has been sent / received, and de-asserts at the end of the packet.
 * In RX, the pin will also de-assert when a packet is discarded due to address or maximum length filtering
 * or when the radio enters RXFIFO_OVERFLOW state. In TX the pin will de-assert if the TX FIFO underflows
 * Settings optimized for low current consumption
 */

#define CC1101_DEFVAL_IOCFG2     0x29        // GDO2 Output Pin Configuration
#define CC1101_DEFVAL_IOCFG1     0x2E        // GDO1 Output Pin Configuration
#define CC1101_DEFVAL_IOCFG0     0x06        // GDO0 Output Pin Configuration
#define CC1101_DEFVAL_FIFOTHR    0x47        // RX FIFO and TX FIFO Thresholds
#define CC1101_DEFVAL_SYNC1      0xB5        // Synchronization word, high byte
#define CC1101_DEFVAL_SYNC0      0x47        // Synchronization word, low byte
#define CC1101_DEFVAL_PKTLEN     0xFF        // Packet Length
#define CC1101_DEFVAL_PKTCTRL1   0x06        // Packet Automation Control
#define CC1101_DEFVAL_PKTCTRL0   0x05        // Packet Automation Control
#define CC1101_DEFVAL_ADDR       0xFF        // Device Address
#define CC1101_DEFVAL_CHANNR     0x00        // Channel Number
#define CC1101_DEFVAL_FSCTRL1    0x08        // Frequency Synthesizer Control
#define CC1101_DEFVAL_FSCTRL0    0x00        // Frequency Synthesizer Control

// Carrier freequency = 433 Mhz
#define CC1101_DEFVAL_FREQ2_433  0x10        // Frequency Control Word, High Byte
#define CC1101_DEFVAL_FREQ1_433  0xA7        // Frequency Control Word, Middle Byte
#define CC1101_DEFVAL_FREQ0_433  0x62        // Frequency Control Word, Low Byte
// Carrier frequency = 868 MHz
#define CC1101_DEFVAL_FREQ2_868  0x21        // Frequency Control Word, High Byte
#define CC1101_DEFVAL_FREQ1_868  0x62        // Frequency Control Word, Middle Byte
#define CC1101_DEFVAL_FREQ0_868  0x76        // Frequency Control Word, Low Byte
// Carrier frequency = 902 MHz
#define CC1101_DEFVAL_FREQ2_915  0x22        // Frequency Control Word, High Byte
#define CC1101_DEFVAL_FREQ1_915  0xB1        // Frequency Control Word, Middle Byte
#define CC1101_DEFVAL_FREQ0_915  0x3B        // Frequency Control Word, Low Byte
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

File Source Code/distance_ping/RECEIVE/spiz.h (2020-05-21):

/**
 * Copyright (c) 2011 Daniel Berenguer <dberenguer@usapiens.com>
 * 
 * This file is part of the panStamp project.
 * 
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
 * Author: Daniel Berenguer
 * Creation date: 03/03/2011
 */

#ifndef _SPI_H
#define _SPI_H

#include "Arduino.h"

/**
 * SPI pins
 */
#define SPI_SS   10     // PB0 = SPI_SS Pin_10
#define SPI_MOSI 11     // PB2 = MOSI Pin_11
#define SPI_MISO 12     // PB3 = MISO 
#define SPI_SCK  13     // PB1 = SCK
#define GDO0     2        // PD2 = INT0

#define PORT_SPI_MISO  PINB
#define BIT_SPI_MISO  4

#define PORT_SPI_SS  PORTB
#define BIT_SPI_SS   2

#define PORT_GDO0  PIND
#define BIT_GDO0  2

/**
 * Macros
 */
// Wait until SPI operation is terminated
#define wait_Spi()  while(!(SPSR & _BV(SPIF)))

/**
 * Class: SPI
 * 
 * Description:
 * Basic SPI class
 */
class SPI
{
  public:
    /**
     * init
     * 
     * SPI initialization
     */
    void init();

    /**
     * send
     * 
     * Send byte via SPI
     * 
     * 'value'  Value to be sent
     * 
     * Return:
     *  Response received from SPI slave
     */
    byte send(byte value);
};
#endif

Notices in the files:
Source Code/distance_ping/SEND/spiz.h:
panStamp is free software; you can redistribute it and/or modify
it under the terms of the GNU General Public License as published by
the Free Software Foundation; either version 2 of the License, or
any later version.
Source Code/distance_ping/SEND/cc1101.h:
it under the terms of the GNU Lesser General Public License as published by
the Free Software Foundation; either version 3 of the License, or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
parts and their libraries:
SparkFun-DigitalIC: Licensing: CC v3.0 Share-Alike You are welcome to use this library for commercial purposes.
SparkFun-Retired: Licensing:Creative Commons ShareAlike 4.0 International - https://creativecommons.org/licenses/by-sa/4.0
